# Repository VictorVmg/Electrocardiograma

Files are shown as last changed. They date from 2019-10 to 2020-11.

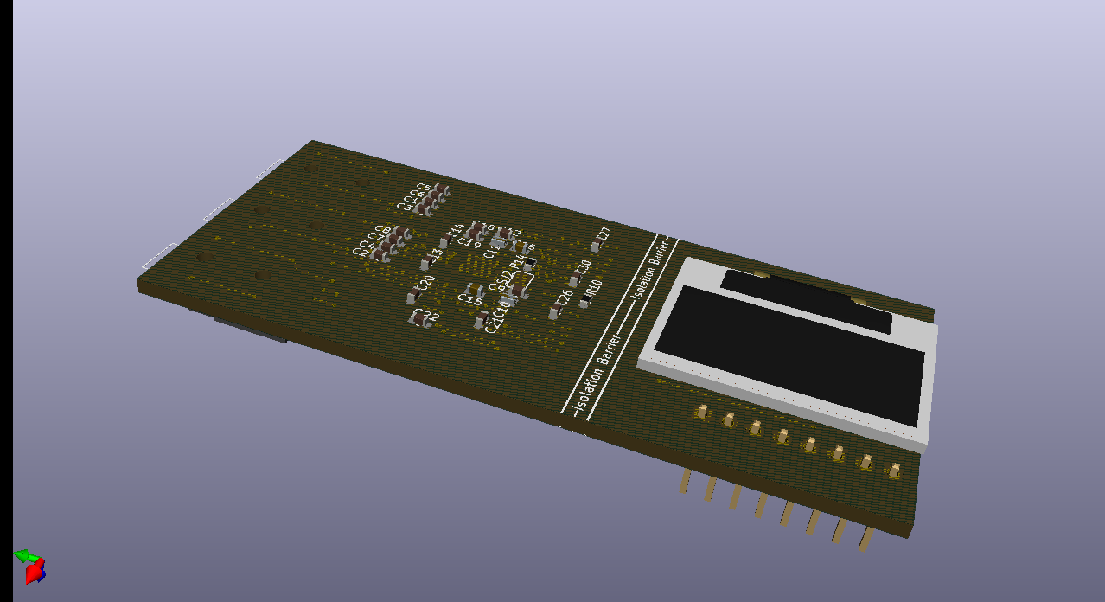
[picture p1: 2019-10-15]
images/electrocardiograma+respiracion back.png

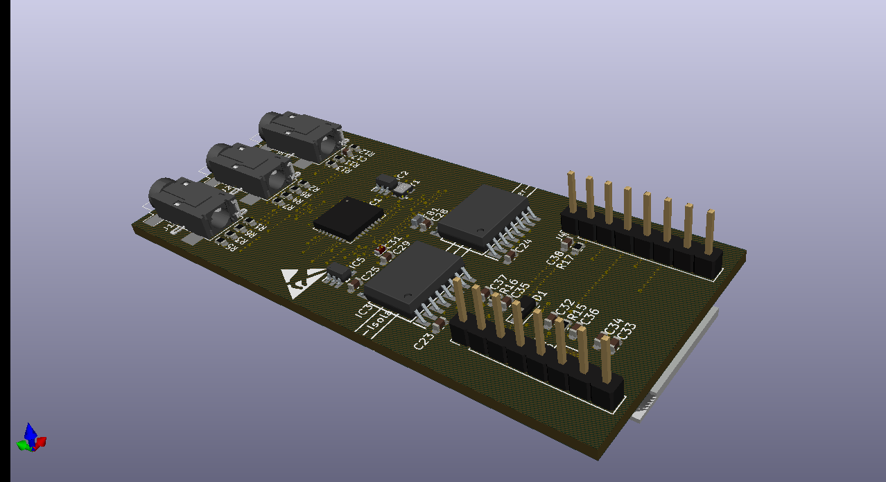
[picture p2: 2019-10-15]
images/electrocardiograma+respiracion front.png

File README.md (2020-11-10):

# Electrocardiograma    
El diseño cuenta con un integrado ADS1292R el cual brinda la capacidad de monitorear la respiración del usuario. Además, se añaden al proyecto una etapa de pruebas la cual hace posible la conexión paciente dispositivo.

## Repositorio

En las carpetas del repositorio se encuentran todos los documentos asociados y que fueron necesarios para realizar este proyecto, entre otras cosas mas.

## Descripción del proyecto 
El proyecto consiste en la creación de un electrocardiograma el cual tenga un tamaño perfecto para el dia a dia del usuario, pequeño, ligero y seguro. Adicionalmente cuenta con un Display OLED el cual permite al usuario monitorear su estado actual asi como el del equipo. El Electrocardiograma cuenta con la compatibilidad de mikro bus el cual expande el potencial de dicho equipo, haciendo que el mismo sea posible ser usado en consultas a distancias y monitoreo profesional por parte del cardiologo que lleve el caso del usuario.

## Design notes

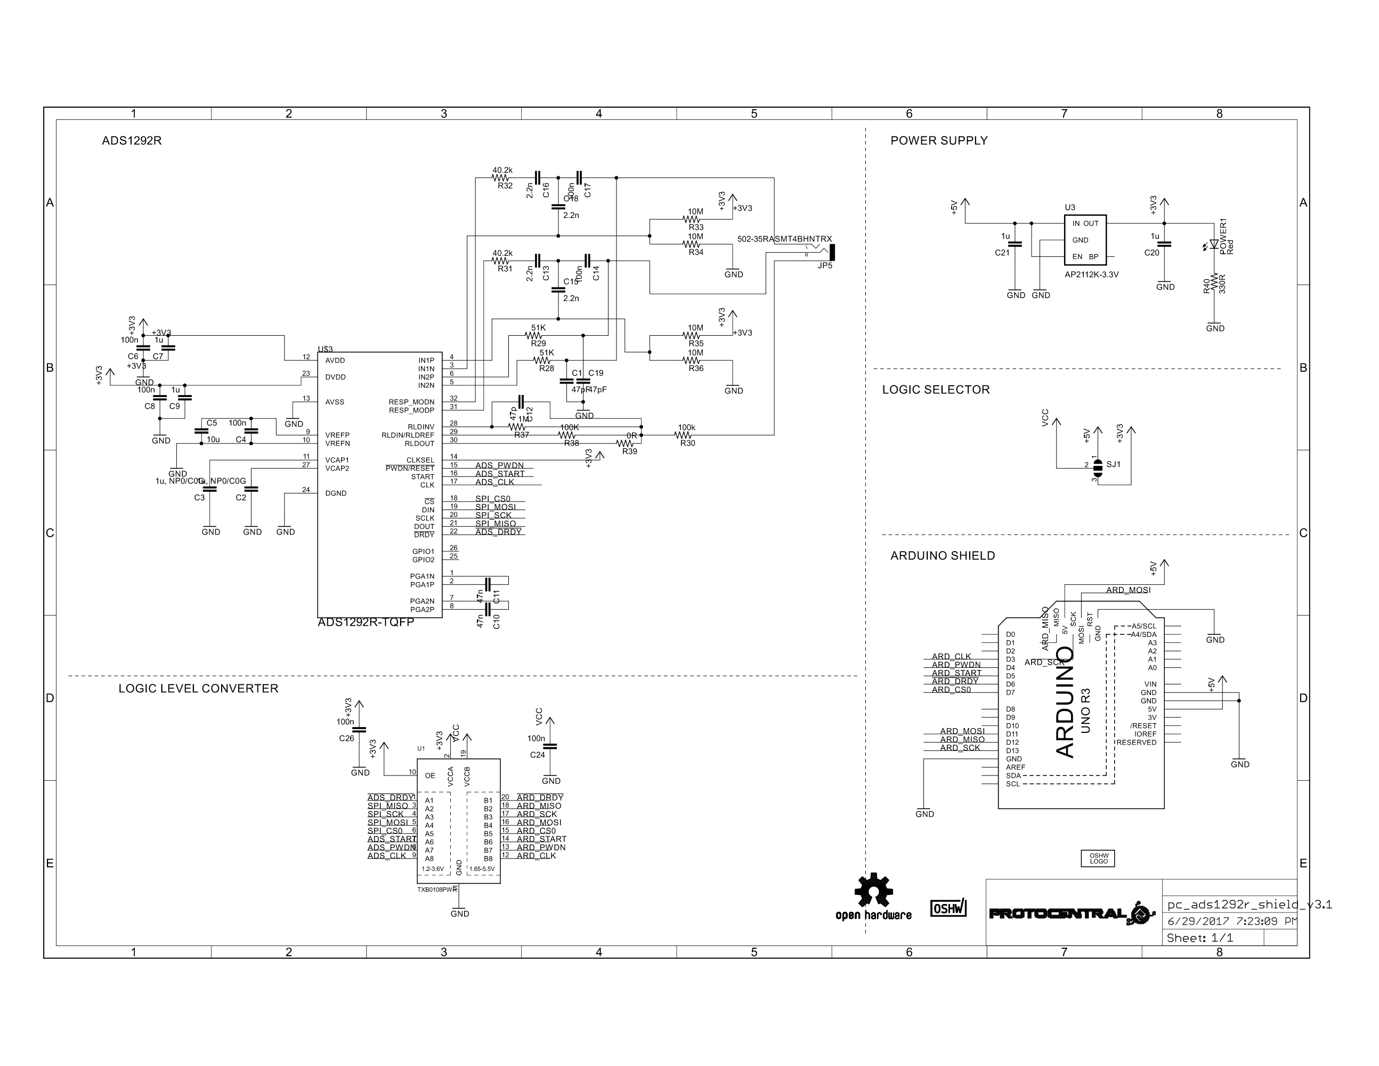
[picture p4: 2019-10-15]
images/ads1292r para arduino.png

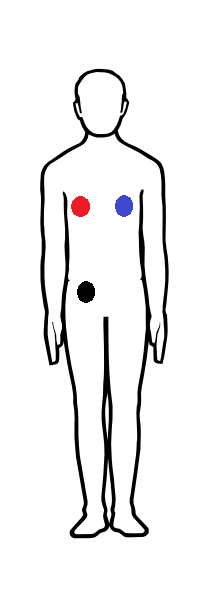
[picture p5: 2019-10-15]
images/body.png

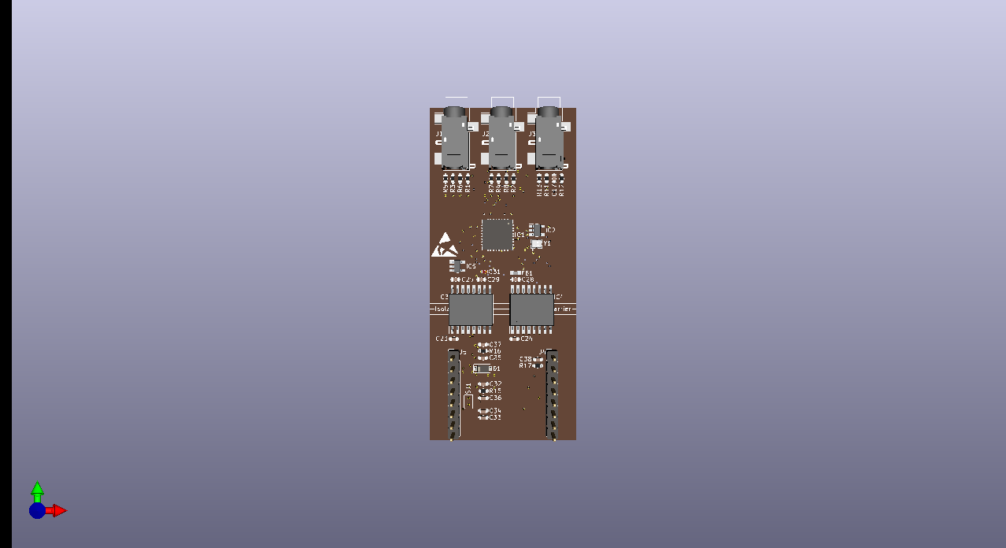
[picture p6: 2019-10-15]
images/electrocardiograma+respiracion.png

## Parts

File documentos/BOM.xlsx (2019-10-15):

Referencia | Valor | Huella | Datasheet | Descripcion | Nombre de Manufactura | Nro. De parte de Manufactura | Nro. Parte Mouser | Precio/Stock en Mouser | Cantidad
> C1, C2 | 0.1uf | Capacitor_SMD:C_0603_1608Metric | https://ve.mouser.com/datasheet/2/212/KEM_C1090_X7R_ESD-1103328.pdf | Multilayer Ceramic Capacitors MLCC - SMD/SMT 16V 0.1uF 0603 X7R 10% | KEMET | C0603C104K4RECTU | 80-C0603C104K4RECTU | 0,11$ | 2
> C3, C4 | 3nF | Capacitor_SMD:C_0603_1608Metric | https://ve.mouser.com/datasheet/2/212/KEM_C1007_X8R_ULTRA_150C_SMD-1102703.pdf | Multilayer Ceramic Capacitors MLCC - SMD/SMT 16V 3000pF 0603 X8R 10% AEC-Q200 | KEMET | C0603C302K4HACAUTO | 80-C0603C302K4HAUTO | 0,20$ | 2
> C5-C8 | 2.2nF | Capacitor_SMD:C_0603_1608Metric | https://ve.mouser.com/datasheet/2/212/KEM_C1023_X7R_AUTO_SMD-1093309.pdf | Multilayer Ceramic Capacitors MLCC - SMD/SMT 50V 2200pF 0603 X7R 5% AEC-Q200 | KEMET | C0603C222J5RACAUTO | 80-C0603C222J5RAUTO | 0,10$ | 4
> C10, C11 | 1uF | footprints-SamacSys:capacitor invertido | http://www.yageo.com/documents/recent/UPY-X5R_X7R_CL_6.3V-to-50V_1.pdf | Multilayer Ceramic Capacitors MLCC - SMD/SMT 100nF 10V X7R 10% | YAGEO | CL0306KRX7R6BB104 | 603-CL306KRX7R6BB104 | 0,29$ | 2
> C9, C12, C18, C20-C22 | 0.1uF | Capacitor_SMD:C_0603_1608Metric | https://ve.mouser.com/datasheet/2/212/KEM_C1090_X7R_ESD-1103328.pdf | Multilayer Ceramic Capacitors MLCC - SMD/SMT 16V 0.1uF 0603 X7R 10% | KEMET | C0603C104K4RECTU | 80-C0603C104K4RECTU | 0,11$ | 6
> C13, C14 | 47nF | Capacitor_SMD:C_0603_1608Metric | https://ve.mouser.com/datasheet/2/212/KEM_C1002_X7R_SMD-1102033.pdf | Multilayer Ceramic Capacitors MLCC - SMD/SMT 25V 0.047uF 0603 X7R 20% | KEMET | C0603C473M3RAC7411 | 80-C0603C473M3RACLR | 0,14$ | 2
> C15, C16 | 1uF | footprints-SamacSys:capacitor C0G | http://www.murata.com/~/media/webrenewal/support/library/catalog/products/capacitor/mlcc/c02e.pdf | Multilayer Ceramic Capacitors MLCC - SMD/SMT 0603 1000pF 50volts C0G 5% | Murata Electronics | GRM1885C1H102JA01D | 81-GRM39C102J50 | 0,10$ (https://www.mouser.com/Search/Refine.aspx?Keyword=81-GRM39C102J50) | 2
C17 | 10nF | Capacitor_SMD:C_0603_1608Metric | https://ve.mouser.com/datasheet/2/212/KEM_C1023_X7R_AUTO_SMD-1093309.pdf | Multilayer Ceramic Capacitors MLCC - SMD/SMT 50V 0.01uF 0603 X7R 10% AEC-Q200 | KEMET | C0603C103K5RACAUTO7411 | 80-C0603C103K5RAUTLR | 0,20$ | 1
> C19, C23-C26, C35 | 10uF | Capacitor_SMD:C_0603_1608Metric | https://ve.mouser.com/datasheet/2/212/KEM_C1023_X7R_AUTO_SMD-1093309.pdf | Multilayer Ceramic Capacitors MLCC - SMD/SMT 50V 0.01uF 0603 X7R 10% AEC-Q200 | KEMET | C0603C103K5RACAUTO7411 | 80-C0603C103K5RAUTLR | 0,20$ | 6
> C27, C28, C30, C32-C34, C36 | 1uF | Capacitor_SMD:C_0603_1608Metric | https://ve.mouser.com/datasheet/2/212/KEM_C1023_X7R_AUTO_SMD-1093309.pdf | Multilayer Ceramic Capacitors MLCC - SMD/SMT 10V 1uF X7R 20% 0603 AEC-Q200 | KEMET | C0603C105M8RACAUTO | 80-C0603C105M8RAUTO | 0,24$ | 7
C29 | 10nF | Capacitor_SMD:C_0603_1608Metric | https://ve.mouser.com/datasheet/2/212/KEM_C1002_X7R_SMD-1102033.pdf | Multilayer Ceramic Capacitors MLCC - SMD/SMT 50V 0.01uF 0603 X7R 10% | KEMET | C0603C103K5RAC7081 | 80-C0603C103K5R7081 | 0,11$ | 1
C31 | 1uF_EMIFIL | footprints-SamacSys:NFM18PS | https://ve.mouser.com/datasheet/2/281/E15251-1527158.pdf | Feed Through Capacitors 0603 1.0uF | Murata Electronics | NFM18PS105R0J3D | 81-NFM18PS105R0J3D | 0.16 | 1
C37 | 2.2uF/16V | Capacitor_SMD:C_0603_1608Metric | https://ve.mouser.com/datasheet/2/40/tac-776418.pdf | Tantalum Capacitors - Solid SMD 16V 2.2uF 20% 0603 ESR= 7.5 Ohms | AVX | TACL225M016XTA | 581-TACL225M016XTA | 2,48$ | 1
C38 | 4.7uF | Capacitor_SMD:C_0603_1608Metric | https://ve.mouser.com/datasheet/2/212/KEM_C1006_X5R_SMD-1103249.pdf | Multilayer Ceramic Capacitors MLCC - SMD/SMT 6.3V 4.7uF 0603 X5R 10% | KEMET | C0603C475K9PAC7411 | 80-C0603C475K9P7411 | 0,55$ | 1
D1 | 1N4148W | Diode_SMD:D_SOD-123 | https://www.vishay.com/docs/85748/1n4148w.pdf | Diodes - General Purpose, Power, Switching SMD Switching Diode Single | Central Semiconductor | CMHD4448 TR | 610-CMHD4448 | 0,70$ | 1
FB1 | BLM18PG121SZ1D | footprints-SamacSys:BLM18PG121SZ1D | http://www.murata.com/~/media/webrenewal/support/library/catalog/products/emc/emifil/c31e.ashx?la=en-gb | BL Chip Ferrite Bead 0603 | Murata Electronics | BLM18PG121SZ1D | 81-BLM18PG121SZ1D | 0,11$ (https://www.mouser.com/Search/Refine.aspx?Keyword=81-BLM18PG121SZ1D) | 1
IC1 | ADS1292RIPBS-SamacSys_Parts | Package_DFN_QFN:QFN-32-1EP_7x7mm_P0.65mm_EP4.65x4.65mm_ThermalVias | http://www.ti.com/lit/ds/symlink/ads1292r.pdf | Analog Front End - AFE 2-Channel,24B ADC | Texas Instruments | ADS1292RIPBS | 595-ADS1292RIPBS | 10,15$ (https://www.mouser.com/Search/Refine.aspx?Keyword=595-ADS1292RIPBS) | 1
IC2 | OPA197 | footprints-SamacSys:OPAMP197IDBVR | http://www.ti.com/lit/ds/symlink/opa197.pdf | Precision Amplifiers Precision RRIO 36V Low IB, Low Vos, Low | Texas Instruments | OPA197IDGKT | 595-OPA197IDGKT | 1,22$ (https://www.mouser.com/Search/Refine.aspx?Keyword=584-AD8605ARTZ-R7) | 1
IC3 | ISOW7842DWER-SamacSys_Parts | footprints-SamacSys:ISOW7841FDWER | http://www.ti.com/lit/ds/symlink/isow7842.pdf | Digital Isolators Reinforced Dig. Isolator with int. power | Texas Instruments | ISOW7842DWER | 595-ISOW7842DWER | 5,61$ (https://www.mouser.com/Search/Refine.aspx?Keyword=595-ISOW7842DWER) | 1
IC4 | ISOW7841FDWER-SamacSys_Parts | footprints-SamacSys:ISOW7841FDWER | http://www.ti.com/lit/ds/symlink/isow7841.pdf | Digital Isolators HE Low-Emissions Reinforced Digi Iso | Texas Instruments | ISOW7841FDWER | 595-ISOW7841FDWER | 10,26$ (https://www.mouser.com/Search/Refine.aspx?Keyword=595-ISOW7841FDWER) | 1
IC5 | LP3985IM5-3.0_NOPB-SamacSys_Parts | footprints-SamacSys:LP3985IM5-3.0_NOPB | http://www.ti.com/lit/ds/symlink/lp3985.pdf | LDO Voltage Regulators 150Ma Low Noise CMOS LDO | Texas Instruments | LP3985IM5-3.0/NOPB | 926-3985IM5-3.0/NOPB | 0,64$ (https://www.mouser.com/Search/Refine.aspx?Keyword=926-3985IM5-3.0%2FNOPB) | 1
> J1-J3 | AudioJack3 | Connector_Audio:Jack_3.5mm_CUI_SJ-3523-SMT_Horizontal | https://ve.mouser.com/datasheet/2/670/sj-352x-smt_series-1313220.pdf | Phone Connectors Audio Jacks | CUI | SJ-3523-SMT-TR | 490-SJ-3523-SMT-TR | 0,89$ | 3
> J4, J5 | Conn_01x08 | Connector_PinHeader_2.54mm:PinHeader_1x08_P2.54mm_Vertical | https://ve.mouser.com/datasheet/2/18/77311-1266344.pdf | Headers & Wire Housings 8P STR SR TMT HDR .76 AU .48IN LENGTH | Amphenol FCI | 77311-124-08LF | 649-77311-124-08LF | 0,59$ | 2
> R1, R2 | 51.1K | Resistor_SMD:R_0603_1608Metric | https://ve.mouser.com/datasheet/2/392/n_catalog_partition01_en-1140338.pdf | Thin Film Resistors - SMD 1/10W 51.1K Ohm 0.1% 0603 10ppm | Susumu | RG1608N-5112-B-T5 | 754-RG1608N-5112-BT5 | 0,17$ | 2
> R3, R4 | 40.2K | Resistor_SMD:R_0603_1608Metric | https://ve.mouser.com/datasheet/2/392/n_catalog_partition01_en-1140338.pdf | Thin Film Resistors - SMD 1/10W 40.2K Ohm .05% 0603 25ppm | Susumu | RG1608P-4022-W-T5 | 754-RG1608P-4022-WT5 | 0,16$ | 2
> R5-R8 | 10M | Resistor_SMD:R_0603_1608Metric | https://ve.mouser.com/datasheet/2/418/NG_DS_1773204-3_1-1358553.pdf | Thick Film Resistors - SMD CRGCQ 0603 10M 5% SMD Resistor | TE Connectivity | CRGCQ0603J10M | 279-CRGCQ0603J10M | 0,11$ | 4
> R11, R13 | 100K | Resistor_SMD:R_0603_1608Metric | https://ve.mouser.com/datasheet/2/418/NG_DS_9-1773463-9_A-1358566.pdf | Thick Film Resistors - SMD CRGP 0603 100K 1% SMD Resistor | TE Connectivity | CRGP0603F100K | 279-CRGP0603F100K | 0,10$ | 2
R12 | 1M | Resistor_SMD:R_0603_1608Metric | https://ve.mouser.com/datasheet/2/315/AOA0000C334-1314047.pdf | Thick Film Resistors - SMD 0603 1% 1.0Mohm Anti-Sulfur AEC-Q200 | Panasonic | ERJ-U03F1004V | 667-ERJ-U03F1004V | 0,13$ | 1
> R10, R14 | 0 | Resistor_SMD:R_0603_1608Metric | https://ve.mouser.com/datasheet/2/315/AOA0000C301-1488782.pdf | Thick Film Resistors - SMD 0603 Zero Ohms | Panasonic | ERJ-3GEY0R00V | 667-ERJ-3GEY0R00V | 0.1 | 2
R15 | 10K | Resistor_SMD:R_0603_1608Metric | https://ve.mouser.com/datasheet/2/418/NG_DS_9-1773463-9_A-1358566.pdf | Thick Film Resistors - SMD CRGP 0603 10K 1% SMD Resistor | TE Connectivity | CRGP0603F10K | 279-CRGP0603F10K | 0,10$ | 1
R16 | 390K | Resistor_SMD:R_0603_1608Metric | https://ve.mouser.com/datasheet/2/418/NG_DS_9-1773463-9_A-1358566.pdf | Thick Film Resistors - SMD CRGP 0603 390K 1% SMD Resistor | TE Connectivity | CRGP0603F390K | 279-CRGP0603F390K | 0,10$ | 1
R17 | 1K | Resistor_SMD:R_0603_1608Metric | https://ve.mouser.com/datasheet/2/54/bourns_08232018_CHP_datasheet-1393034.pdf | Thick Film Resistors - SMD 1/3W 1Kohms 1% 100ppm Ultra HP Chip | Bourns | CHP0603-FX-1001ELF | 652-CHP0603FX1001ELF | 0,36$ | 1
> SJ1, SJ2 | JUMPER | footprints-SamacSys:SOLDERJUMPER_REFLOW_NOPASTE | https://ve.mouser.com/datasheet/2/447/PYu-PA0402_L_51_RoHS_0-1480212.pdf | Current Sense Resistors - SMD 0 ohm Jumper 1/16W | YAGEO | PA0402-R-070RL | 603-PA0402-R-070RL | 0,81$ | 2
U1 | UG-2864HSWEG01 | footprints-SamacSys:display |  |  |  |  |  |  | 1
Y1 | SG-210STF_40.0000ML3 | footprints-SamacSys:oscilator | https://ve.mouser.com/datasheet/2/137/G-210STF_en-1003240.pdf | Standard Clock Oscillators 40MHz 50ppm -40C +85C | Epson Timing | SG-210STF 40.0000ML3 | 732-SG210STF40.0L3 | 1,17$ (https://www.mouser.com/Search/Refine.aspx?Keyword=732-SG210STF40.0L3) | 1

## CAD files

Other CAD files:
Librerias: Esquemático+PCB/3D/BLM18PG121SZ1D.stl

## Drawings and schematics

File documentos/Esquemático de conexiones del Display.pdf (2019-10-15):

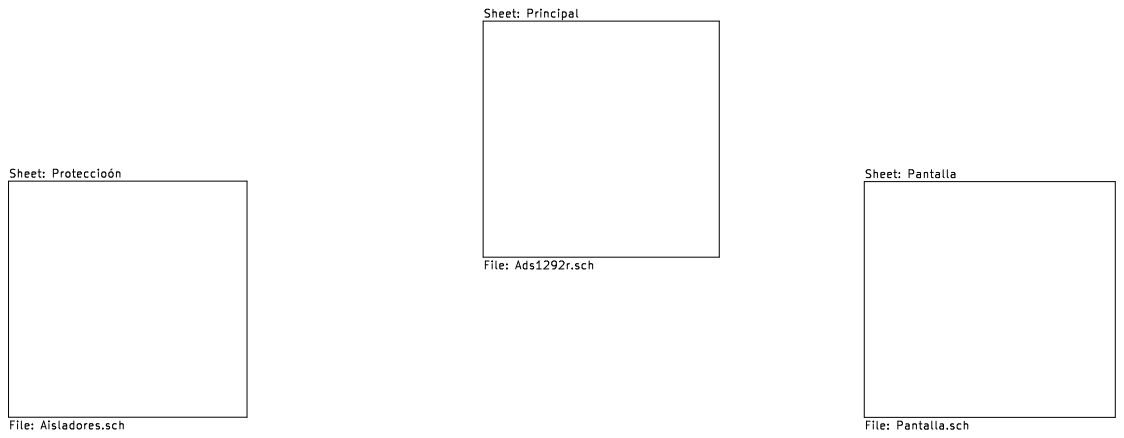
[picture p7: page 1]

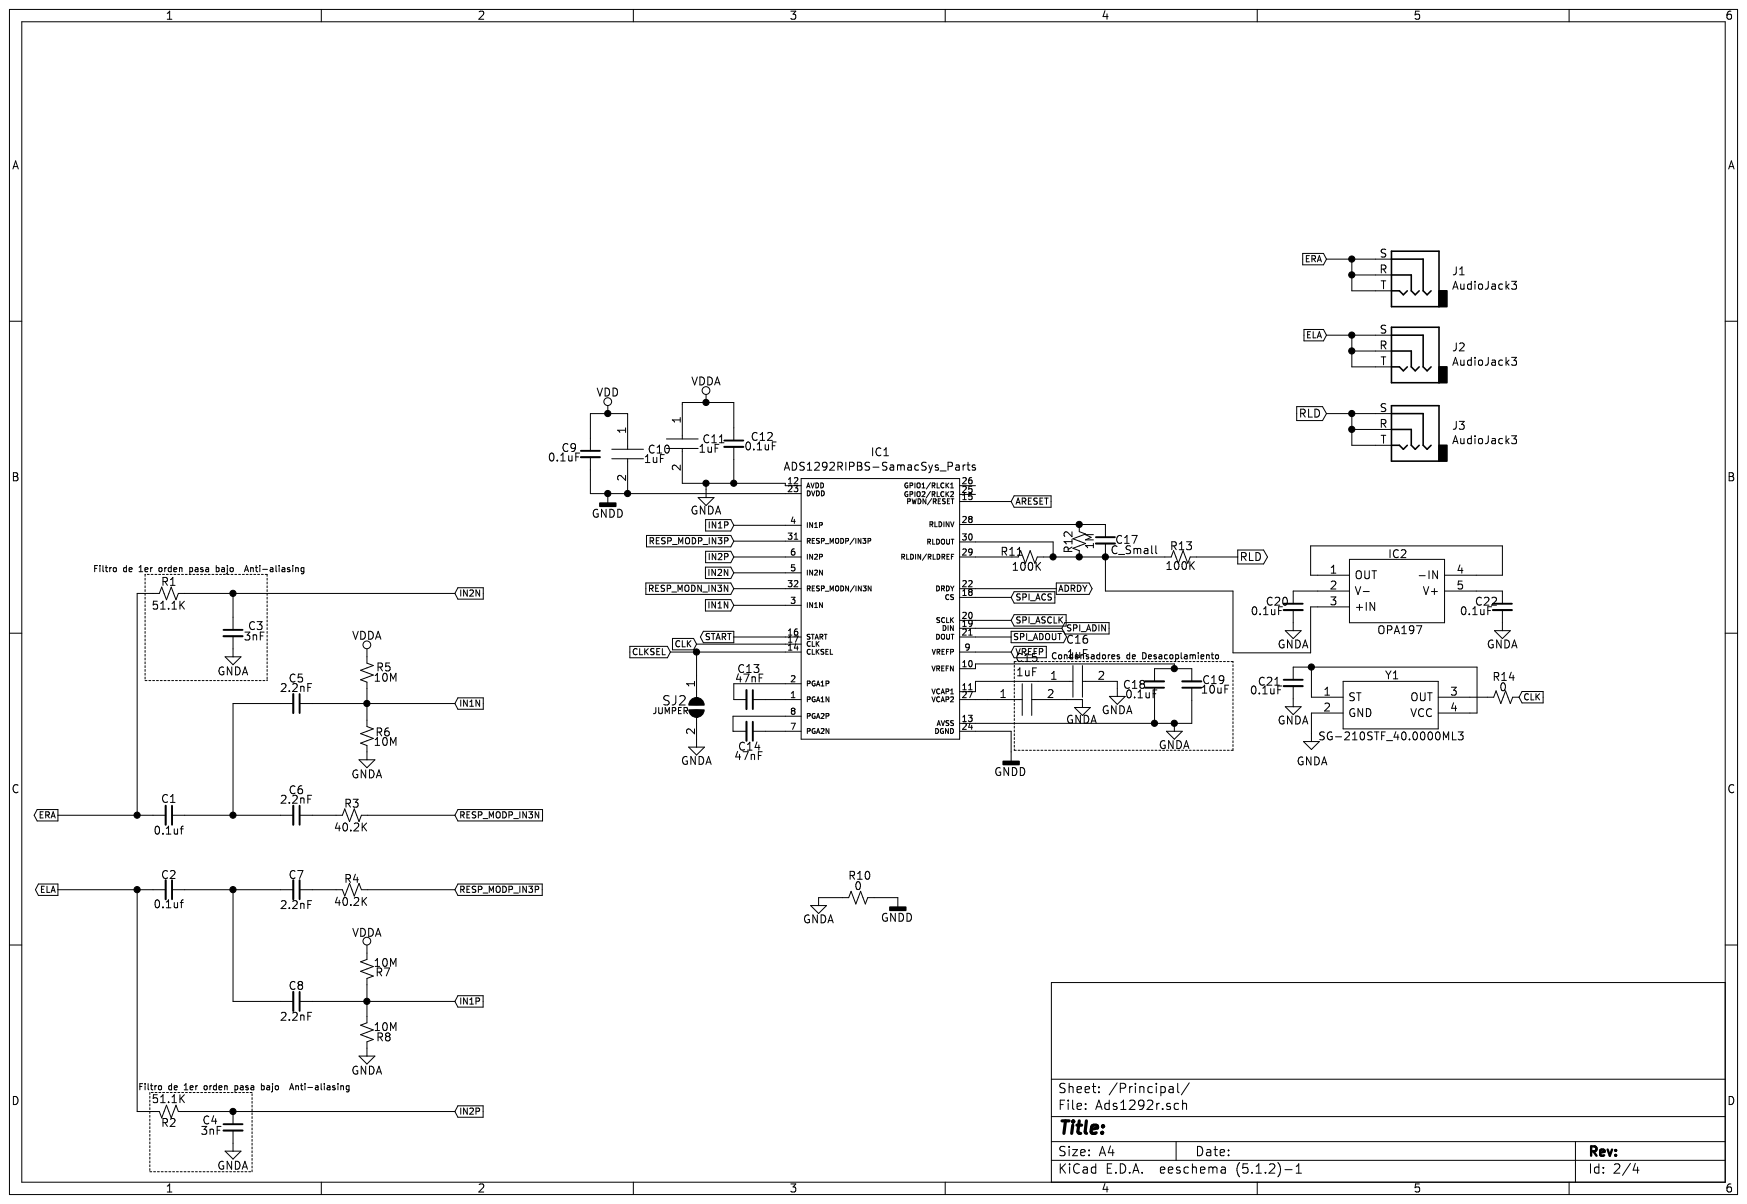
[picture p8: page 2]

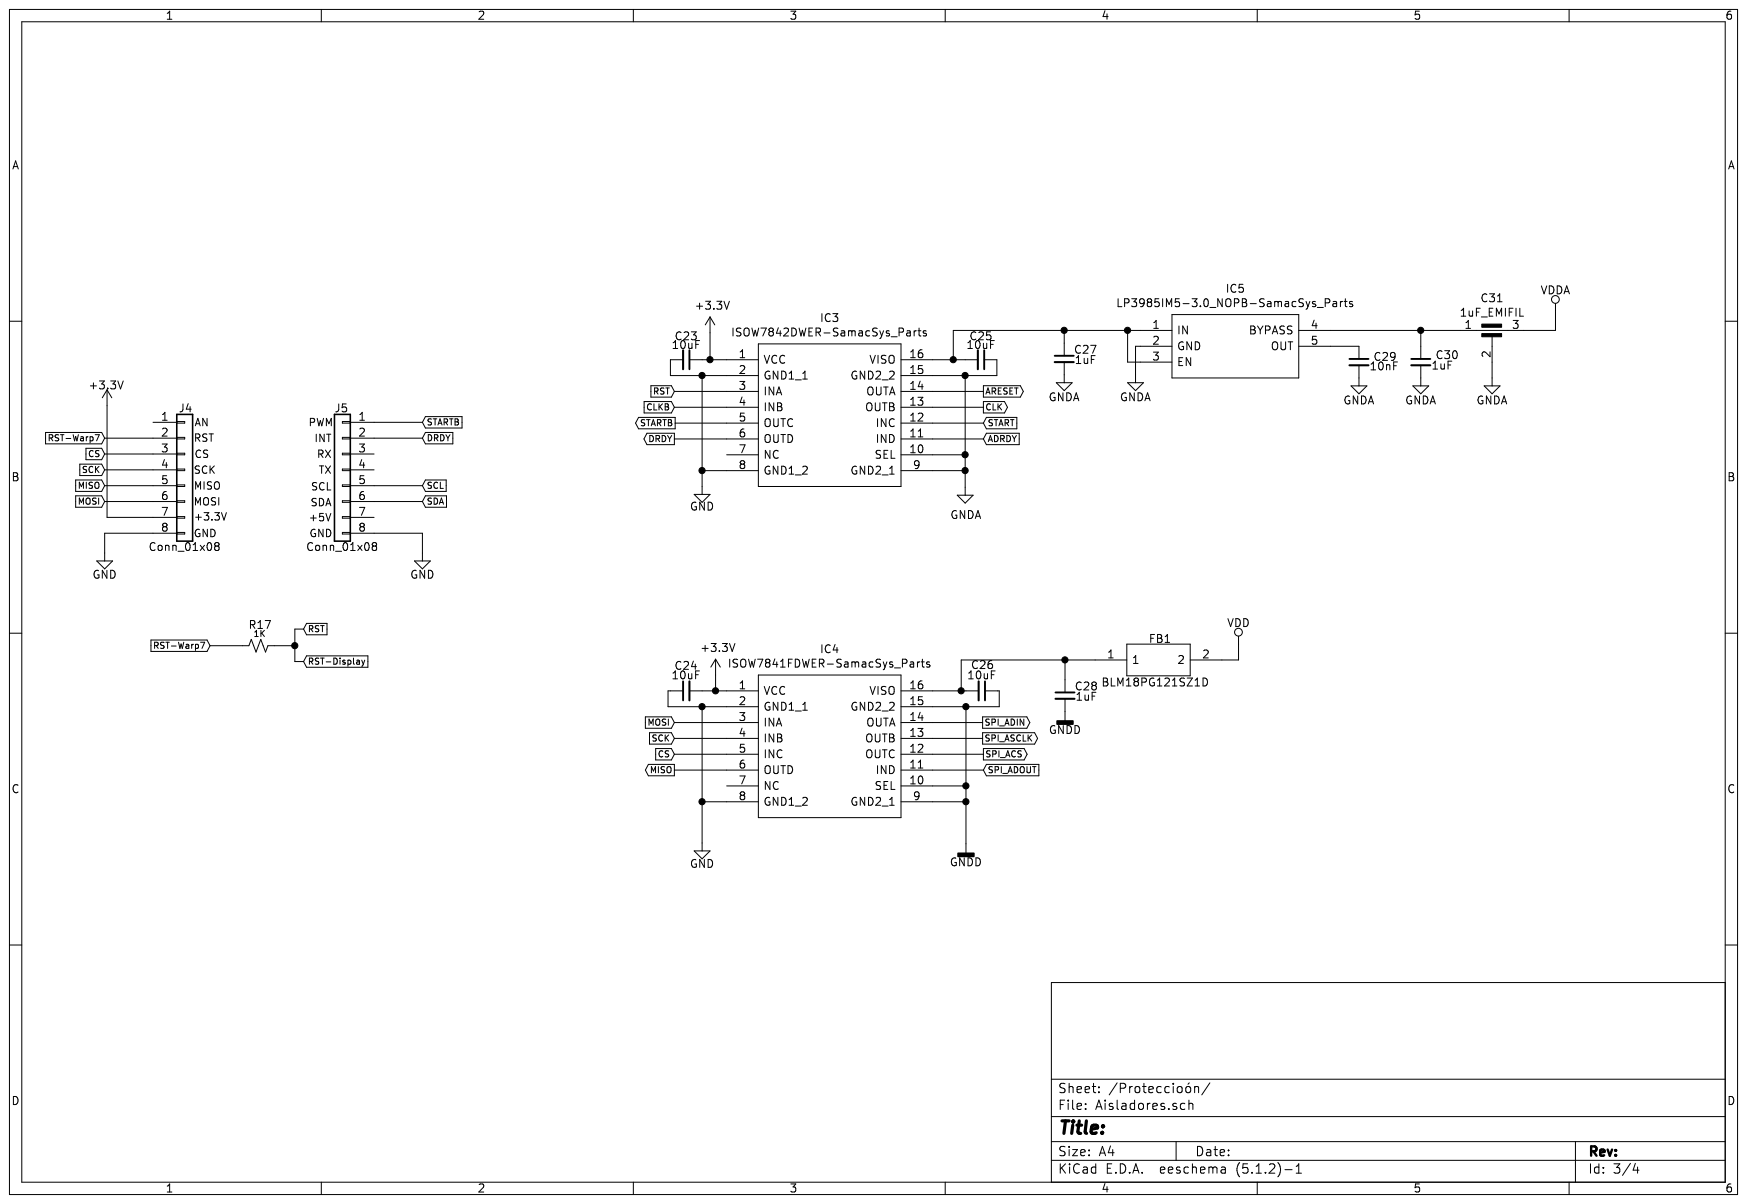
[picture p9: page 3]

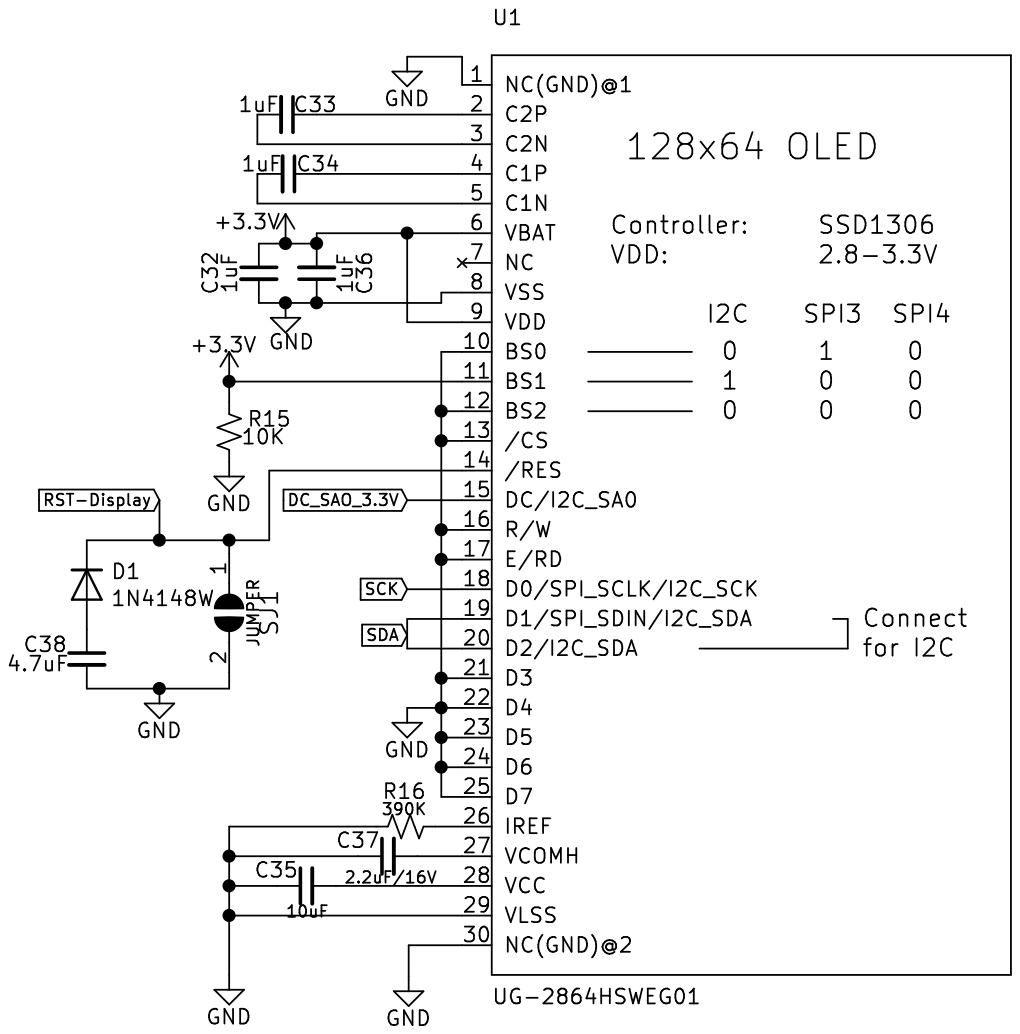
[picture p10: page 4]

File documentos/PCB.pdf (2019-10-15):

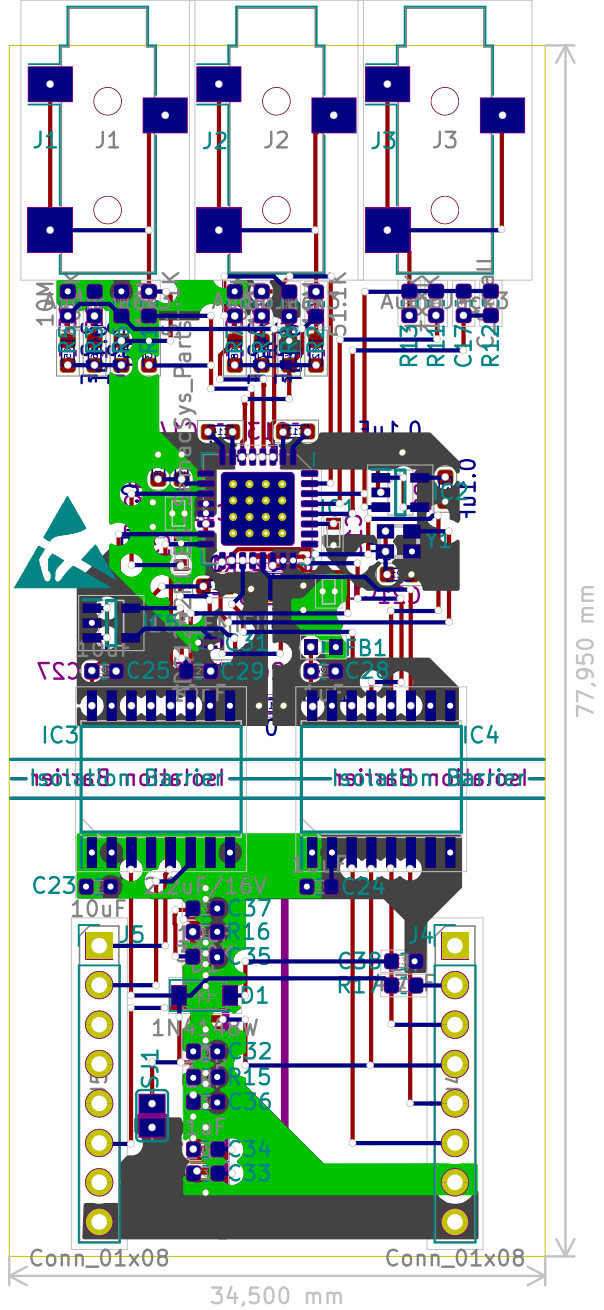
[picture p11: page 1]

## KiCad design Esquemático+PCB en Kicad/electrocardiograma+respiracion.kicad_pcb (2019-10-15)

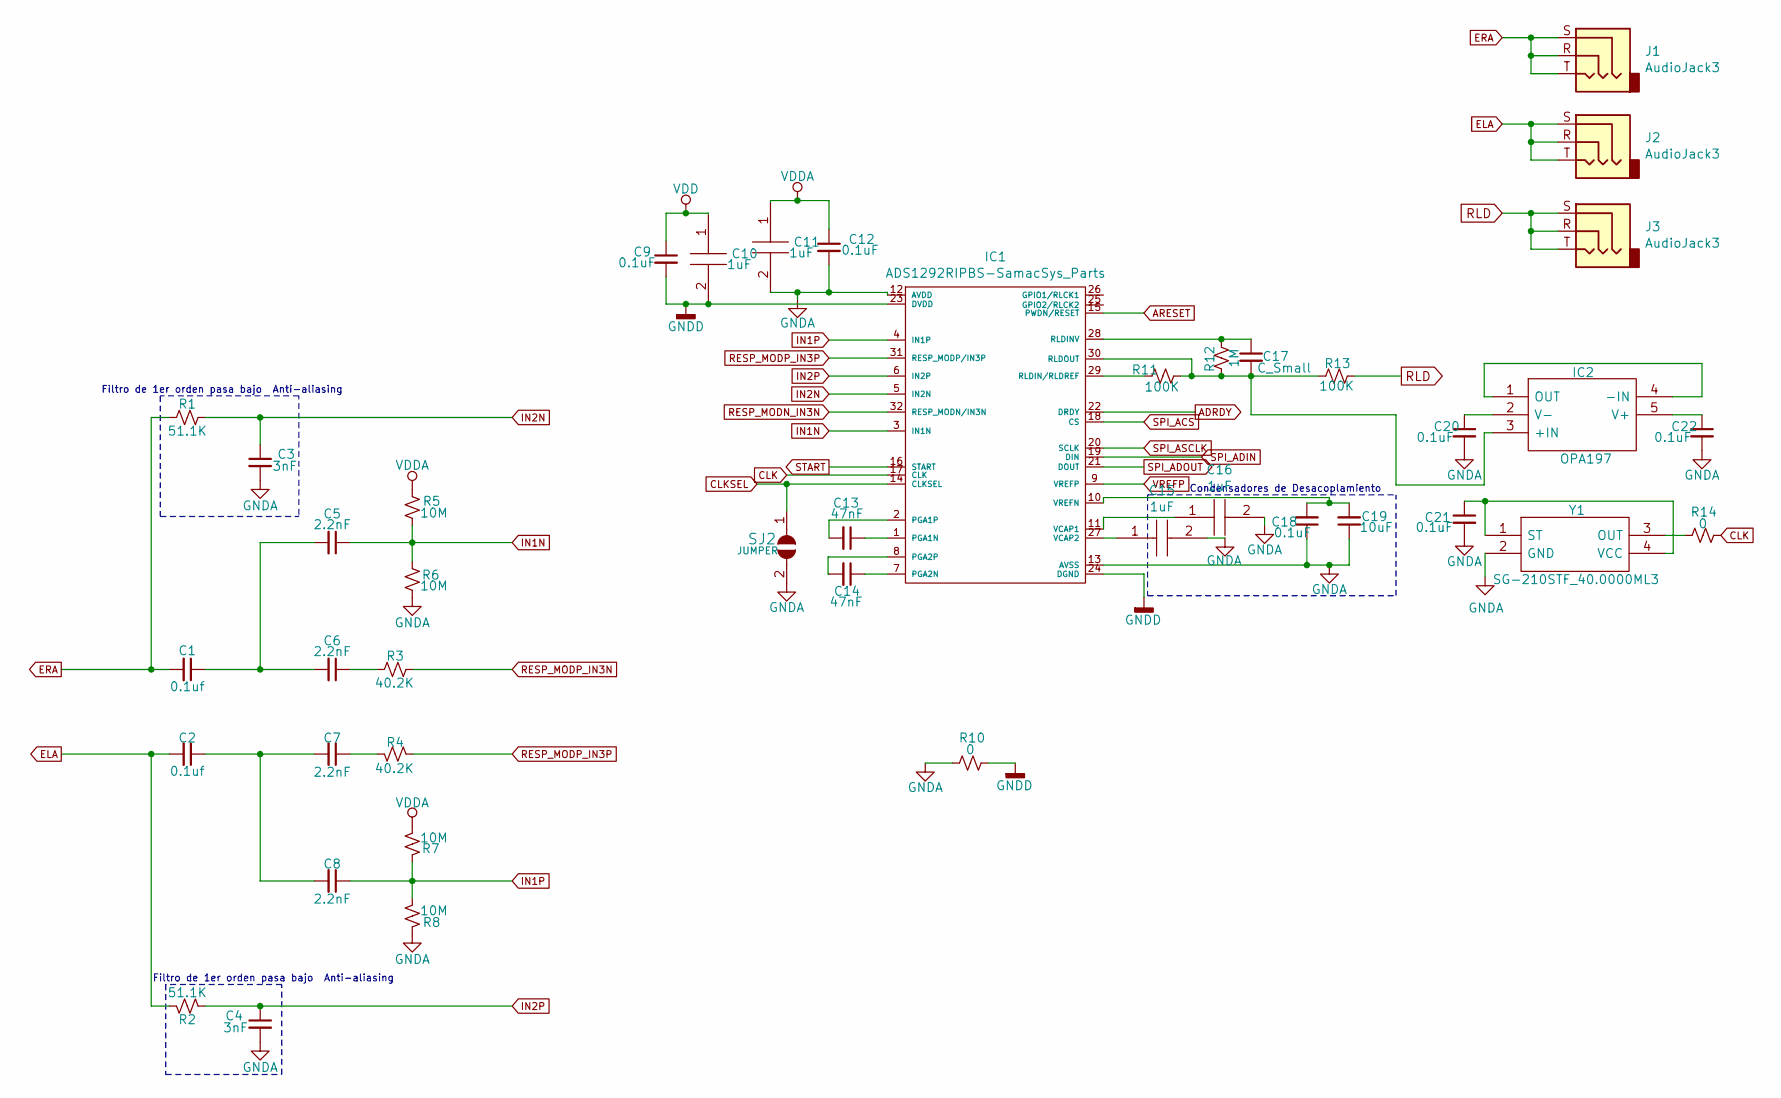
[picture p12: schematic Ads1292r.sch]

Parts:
C1, C2: 0.1uf; C_0603_1608Metric
C3, C4: 3nF; C_0603_1608Metric
C5, C6, C7, C8: 2.2nF; C_0603_1608Metric
C9, C12, C18, C20, C21, C22: 0.1uF; C_0603_1608Metric
C10, C11: 1uF; capacitor invertido; Manufacturer_Part_Number CL0306KRX7R6BB104; Mouser Part Number 603-CL306KRX7R6BB104
C13, C14: 47nF; C_0603_1608Metric
C15, C16: 1uF; capacitor C0G; Manufacturer_Part_Number GRM1885C1H102JA01D; Mouser Part Number 81-GRM39C102J50
C17: C_Small; C_0603_1608Metric
C19: 10uF; C_0603_1608Metric
IC1: ADS1292RIPBS-SamacSys_Parts; QFN-32-1EP_7x7mm_P0.65mm_EP4.65x4.65mm_ThermalVias; Manufacturer_Part_Number ADS1292RIPBS; Mouser Part Number 595-ADS1292RIPBS
IC2: OPA197; OPAMP197IDBVR; Manufacturer_Part_Number AD8605ARTZ-REEL7; Mouser Part Number 584-AD8605ARTZ-R7
J1, J2, J3: AudioJack3; Jack_3.5mm_CUI_SJ-3523-SMT_Horizontal
R1, R2: 51.1K; R_0603_1608Metric
R3, R4: 40.2K; R_0603_1608Metric
R5, R6, R7, R8: 10M; R_0603_1608Metric
R10, R14: 0; R_0603_1608Metric
R11, R13: 100K; R_0603_1608Metric
R12: 1M; R_0603_1608Metric
SJ2: JUMPER; SOLDERJUMPER_REFLOW_NOPASTE
Y1: SG-210STF_40.0000ML3; oscilator; Manufacturer_Part_Number SG-210STF 40.0000ML3; Mouser Part Number 732-SG210STF40.0L3

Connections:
ADRDY: IC1.22 (DRDY); also elsewhere on the board
ARESET: IC1.15 (PWDN/RESET); also elsewhere on the board
CLK: IC1.17 (CLK), R14.1; also elsewhere on the board
CLKSEL: IC1.14 (CLKSEL), SJ2.1
ELA: C2.2, J2.R, J2.S, J2.T, R2.2
ERA: C1.2, J1.R, J1.S, J1.T, R1.2
GNDA: C3.2, C4.2, C11.2, C12.2, C15.2, C16.2, C18.1, C19.1, C20.2, C21.2, C22.2, IC1.12 (AVDD), IC1.13 (AVSS), R6.2, R8.1, R10.2, SJ2.2, Y1.2 (GND); also elsewhere on the board
GNDD: C9.2, C10.2, IC1.23 (DVDD), IC1.24 (DGND), R10.1; also elsewhere on the board
IN1N: C5.1, IC1.3 (IN1N), R5.2, R6.1
IN1P: C8.1, IC1.4 (IN1P), R7.1, R8.2
IN2N: C3.1, IC1.5 (IN2N), R1.1
IN2P: C4.1, IC1.6 (IN2P), R2.1
unnamed: C1.1, C5.2, C6.2
unnamed: C2.1, C7.2, C8.2
unnamed: C6.1, R3.2
unnamed: C7.1, R4.2
unnamed: C13.1, IC1.1 (PGA1N)
unnamed: C13.2, IC1.2 (PGA1P)
unnamed: C14.1, IC1.7 (PGA2N)
unnamed: C14.2, IC1.8 (PGA2P)
unnamed: C15.1, IC1.27 (VCAP2)
unnamed: C16.1, IC1.11 (VCAP1)
unnamed: C17.1, IC1.28 (RLDINV), R12.2
unnamed: C17.2, IC1.30 (RLDOUT), IC2.3 (+IN), R11.1, R12.1, R13.2
unnamed: C18.2, C19.2, IC1.10 (VREFN)
unnamed: C20.1, IC2.2 (V-)
unnamed: C21.1, Y1.1 (ST), Y1.4 (VCC)
unnamed: C22.1, IC2.5 (V+)
unnamed: IC1.29 (RLDIN/RLDREF), R11.2
unnamed: IC2.1 (OUT), IC2.4 (-IN)
unnamed: R14.2, Y1.3 (OUT)
RESP_MODN_IN3N: IC1.32 (RESP_MODN/IN3N)
RESP_MODP_IN3N: R3.1
RESP_MODP_IN3P: IC1.31 (RESP_MODP/IN3P), R4.1
RLD: J3.R, J3.S, J3.T, R13.1
SPI_ACS: IC1.18 (CS); also elsewhere on the board
SPI_ADIN: IC1.19 (DIN); also elsewhere on the board
SPI_ADOUT: IC1.21 (DOUT); also elsewhere on the board
SPI_ASCLK: IC1.20 (SCLK); also elsewhere on the board
START: IC1.16 (START); also elsewhere on the board
VDD: C9.1, C10.1; also elsewhere on the board
VDDA: C11.1, C12.1, R5.1, R7.2; also elsewhere on the board
VREFP: IC1.9 (VREFP)

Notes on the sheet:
Filtro de 1er orden pasa bajo Anti-aliasing
Condensadores de Desacoplamiento

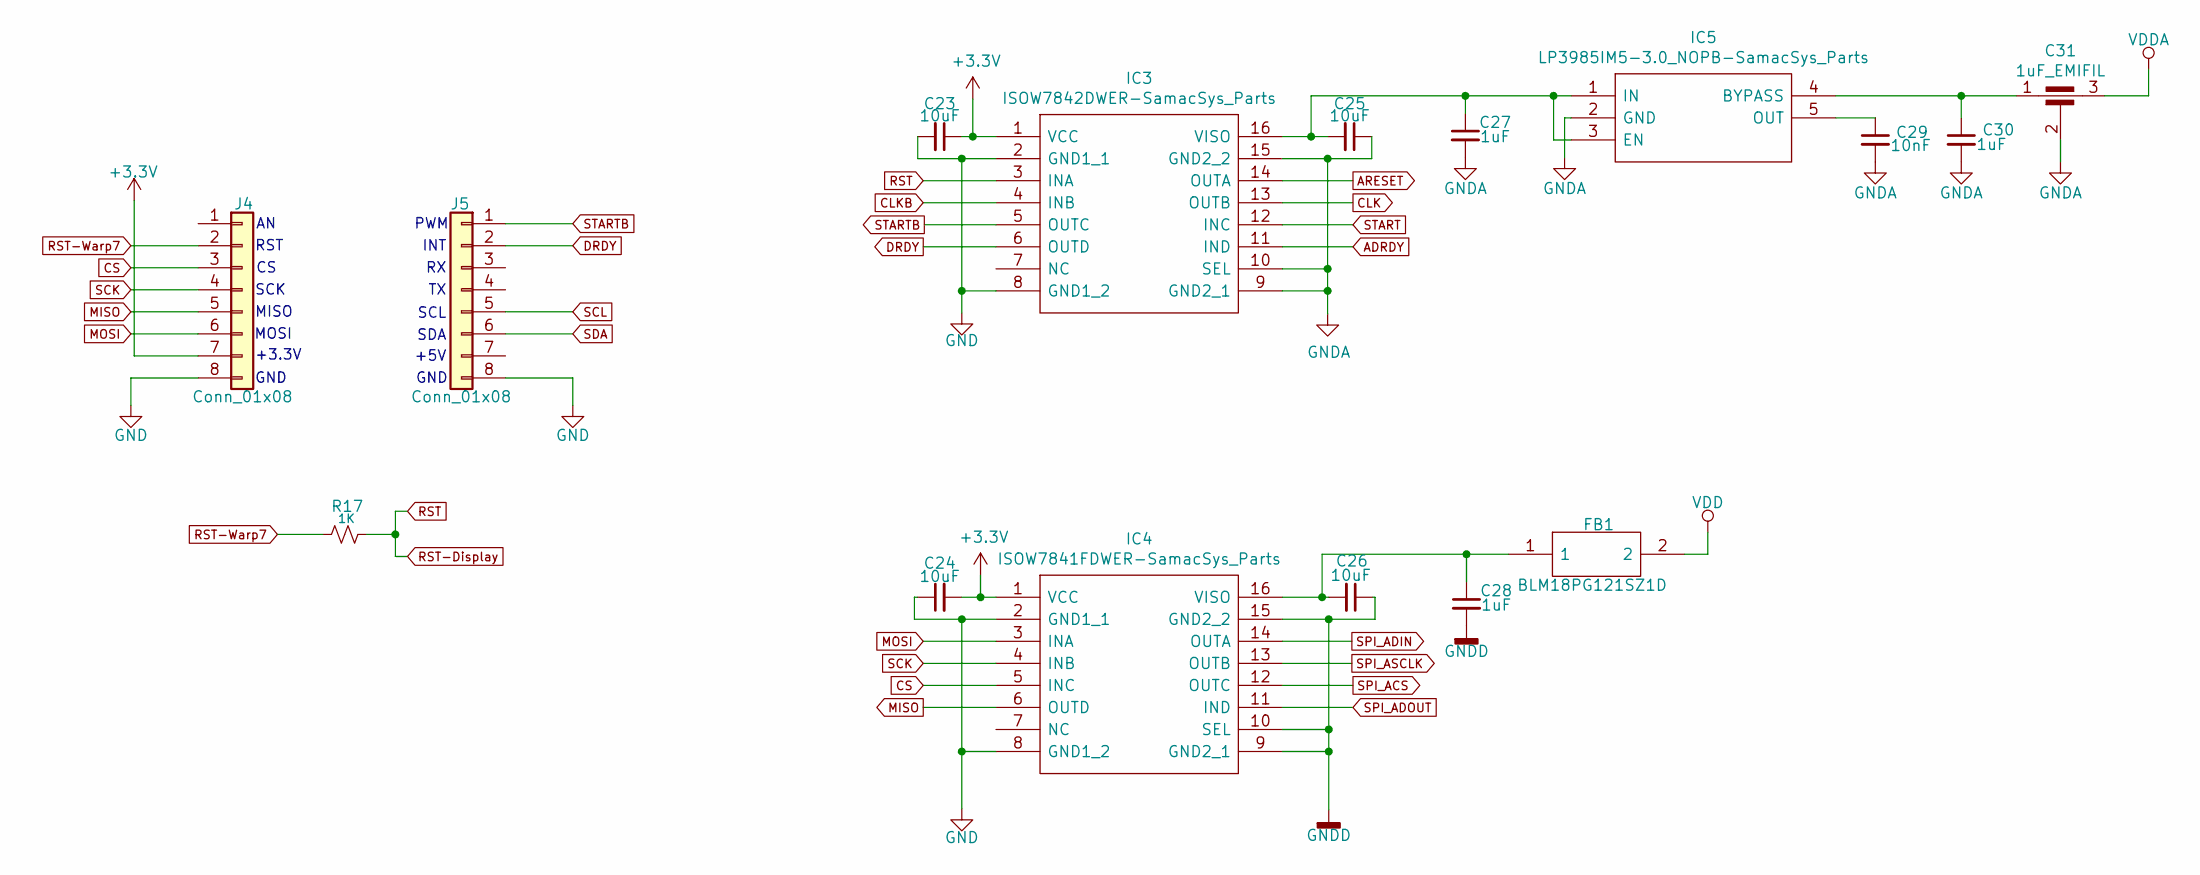
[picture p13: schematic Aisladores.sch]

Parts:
C23, C24, C25, C26: 10uF; C_0603_1608Metric
C27, C28, C30: 1uF; C_0603_1608Metric
C29: 10nF; C_0603_1608Metric
C31: 1uF_EMIFIL; NFM18PS
FB1: BLM18PG121SZ1D; Manufacturer_Part_Number BLM18PG121SZ1D; Mouser Part Number 81-BLM18PG121SZ1D
IC3: ISOW7842DWER-SamacSys_Parts; ISOW7841FDWER; Manufacturer_Part_Number ISOW7842DWER; Mouser Part Number 595-ISOW7842DWER
IC4: ISOW7841FDWER-SamacSys_Parts; ISOW7841FDWER; Manufacturer_Part_Number ISOW7841FDWER; Mouser Part Number 595-ISOW7841FDWER
IC5: LP3985IM5-3.0_NOPB-SamacSys_Parts; LP3985IM5-3.0_NOPB; Manufacturer_Part_Number LP3985IM5-3.0/NOPB; Mouser Part Number 926-3985IM5-3.0/NOPB
J4, J5: Conn_01x08; PinHeader_1x08_P2.54mm_Vertical
R17: 1K; R_0603_1608Metric

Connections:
+3V3: C23.1, C24.2, IC3.1 (VCC), IC4.1 (VCC), J4.7; also elsewhere on the board
ADRDY: IC3.11 (IND); also elsewhere on the board
ARESET: IC3.14 (OUTA); also elsewhere on the board
CLK: IC3.13 (OUTB); also elsewhere on the board
CLKB: IC3.4 (INB)
CS: IC4.5 (INC), J4.3
DRDY: IC3.6 (OUTD), J5.2
GND: C23.2, C24.1, IC3.2 (GND1_1), IC3.8 (GND1_2), IC4.2 (GND1_1), IC4.8 (GND1_2), J4.8, J5.8; also elsewhere on the board
GNDA: C25.1, C27.2, C29.2, C30.2, C31.2, IC3.9 (GND2_1), IC3.10 (SEL), IC3.15 (GND2_2), IC5.2 (GND); also elsewhere on the board
GNDD: C26.1, C28.2, IC4.9 (GND2_1), IC4.10 (SEL), IC4.15 (GND2_2); also elsewhere on the board
MISO: IC4.6 (OUTD), J4.5
MOSI: IC4.3 (INA), J4.6
unnamed: C25.2, C27.1, IC3.16 (VISO), IC5.1 (IN), IC5.3 (EN)
unnamed: C26.2, C28.1, FB1.1, IC4.16 (VISO)
unnamed: C29.1, IC5.5 (OUT)
unnamed: C30.1, C31.1, IC5.4 (BYPASS)
RST: IC3.3 (INA), R17.2; also elsewhere on the board
RST-Warp7: J4.2, R17.1
SCK: IC4.4 (INB), J4.4; also elsewhere on the board
SCL: J5.5
SDA: J5.6; also elsewhere on the board
SPI_ACS: IC4.12 (OUTC); also elsewhere on the board
SPI_ADIN: IC4.14 (OUTA); also elsewhere on the board
SPI_ADOUT: IC4.11 (IND); also elsewhere on the board
SPI_ASCLK: IC4.13 (OUTB); also elsewhere on the board
START: IC3.12 (INC); also elsewhere on the board
STARTB: IC3.5 (OUTC), J5.1
VDD: FB1.2; also elsewhere on the board
VDDA: C31.3; also elsewhere on the board

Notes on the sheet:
RST
SCK
MISO
MOSI
+3.3V
GND
PWM
INT
SCL
SDA
+5V

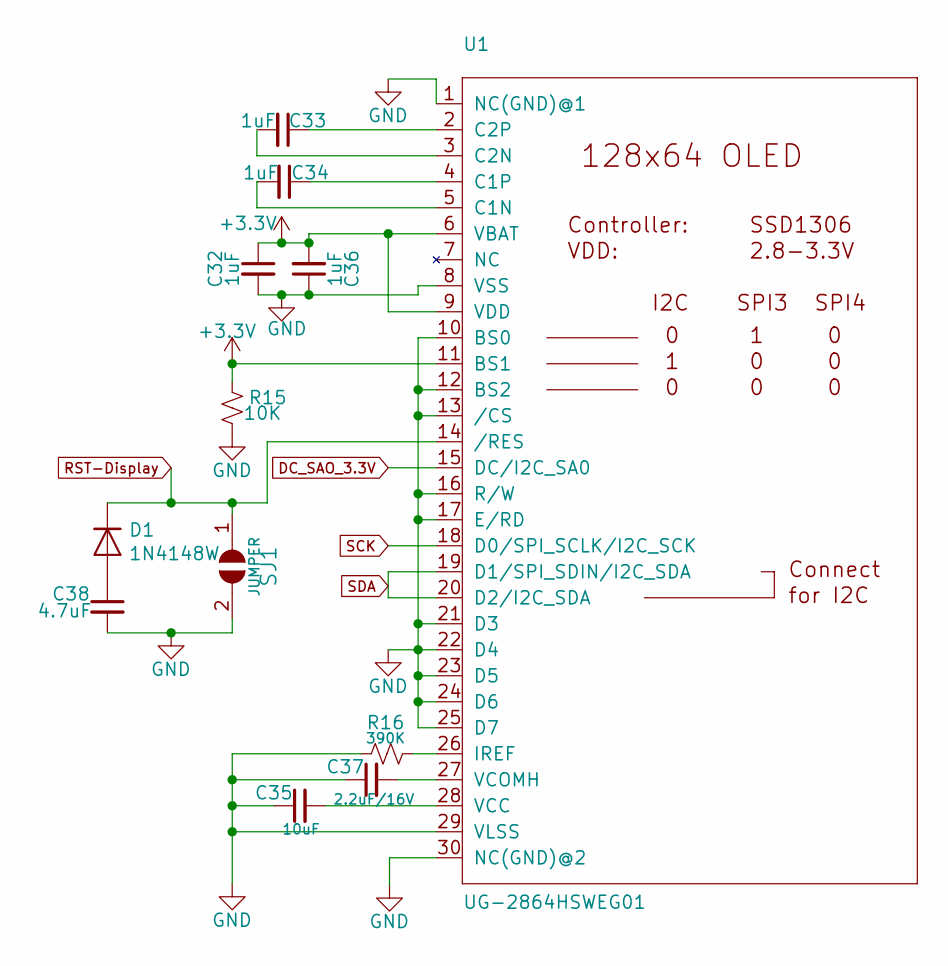
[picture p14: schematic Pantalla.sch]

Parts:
C32, C33, C34, C36: 1uF; C_0603_1608Metric
C35: 10uF; C_0603_1608Metric
C37: 2.2uF/16V; C_0603_1608Metric
C38: 4.7uF; C_0603_1608Metric
D1: 1N4148W; D_SOD-123
R15: 10K; R_0603_1608Metric
R16: 390K; R_0603_1608Metric
SJ1: JUMPER; SOLDERJUMPER_REFLOW_NOPASTE
U1: UG-2864HSWEG01; display

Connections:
+3V3: C32.1, C36.2, R15.2, U1.6 (VBAT), U1.7 (NC), U1.9 (VDD), U1.11 (BS1); also elsewhere on the board
DC_SAO_3.3V: U1.15 (DC/I2C_SA0)
GND: C32.2, C35.1, C36.1, C37.1, C38.2, R15.1, R16.2, SJ1.2, U1.1 (NC(GND)@1), U1.8 (VSS), U1.10 (BS0), U1.12 (BS2), U1.13 (/CS), U1.16 (R/W), U1.17 (E/RD), U1.21 (D3), U1.22 (D4), U1.23 (D5), U1.24 (D6), U1.25 (D7), U1.29 (VLSS), U1.30 (NC(GND)@2); also elsewhere on the board
unnamed: C33.1, U1.2 (C2P)
unnamed: C33.2, U1.3 (C2N)
unnamed: C34.1, U1.4 (C1P)
unnamed: C34.2, U1.5 (C1N)
unnamed: C35.2, U1.28 (VCC)
unnamed: C37.2, U1.27 (VCOMH)
unnamed: C38.1, D1.2 (A)
unnamed: R16.1, U1.26 (IREF)
RST: D1.1 (K), SJ1.1, U1.14 (/RES); also elsewhere on the board
SCK: U1.18 (D0/SPI_SCLK/I2C_SCK); also elsewhere on the board
SDA: U1.19 (D1/SPI_SDIN/I2C_SDA), U1.20 (D2/I2C_SDA); also elsewhere on the board

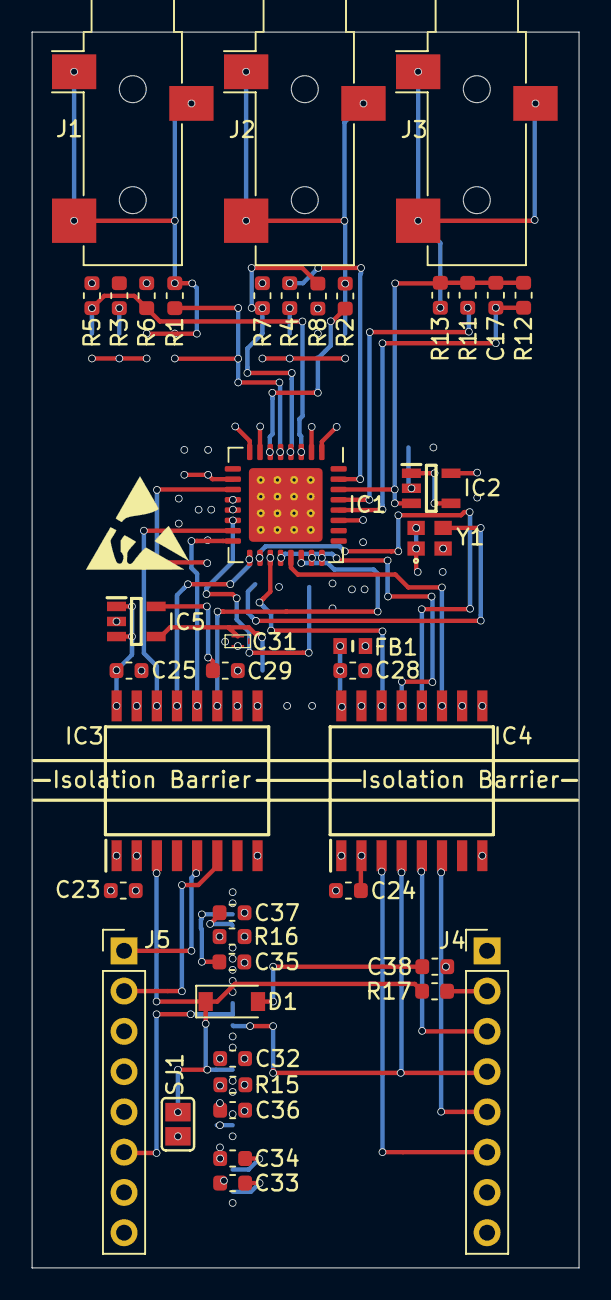
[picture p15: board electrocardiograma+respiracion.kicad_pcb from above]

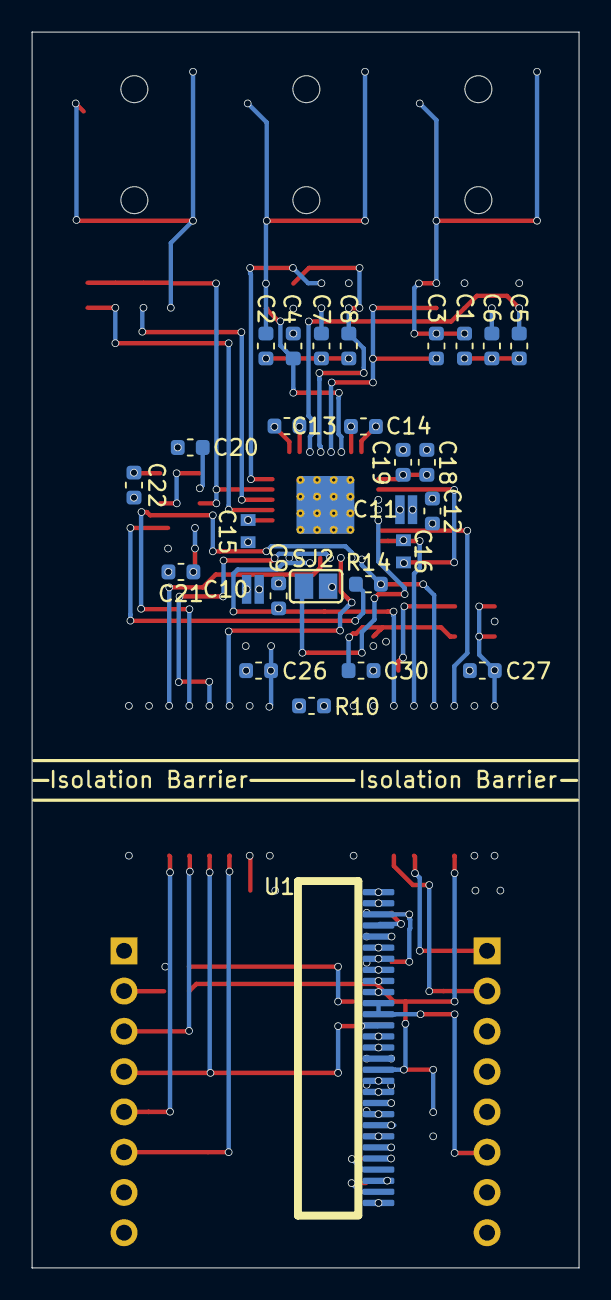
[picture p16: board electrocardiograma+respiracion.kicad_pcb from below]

Board: 4 copper layers, 34.5 x 78.0 mm, 70 parts (28 on the bottom side), 63 nets.

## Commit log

2019-10-15 documentación
    Estos documentos son los necesarios para la operación del circuito. Entre ellos, están los data sheet de los componentes que se consideraron óptimos para la creación del Electrocardiograma.
    [BOM.xlsx]
2019-10-15 Imagenes
    En las Imagenes se encuentra:
    -Conexiones de los tres electrodos
    -Esquemático para Arduino
    -Vista frontal 3D del pcd
    -Vista trasera del
2019-10-15 Librerias
    Las librerias son para el uso en kicad
    [BLM18PG121SZ1D.stl, BLM18PG121SZ1D.stp]
2019-10-15 Esquemáticos mas PCB
    en esta carpeta se encuentran los esquemáticos de:
    - Protecciones
    - Pantalla
    - ADS1292R
    -Extras
2019-10-15 archivos principales
    Esquemáticos, pcb de cuatro (4) capas con sus vistas 3D.
    [Ads1292r.sch, Aisladores.sch, Pantalla.sch, electrocardiograma+respiracion.kicad_pcb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]
